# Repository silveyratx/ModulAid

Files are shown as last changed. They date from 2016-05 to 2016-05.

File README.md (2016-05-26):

# Modulaid

### Overview
ModulAid was born at UT Austin as a Senior Design Project for 5 Electrical Engineering [students](#contributors). Their senior design class was a special section called "Startup Senior Design" and the students thought up their own project rather than doing an industry or faculty sponsored project.

ModulAid extends a smartphone by providing an easy to use interface for many different types of sensors. The main hub plugs into the smartphone via the headphone jack. Through the connection with the headphone jack, the board is able to communicate with the iOS app as well as harvest power. Sensors can then be attached to the shared sensor board. The board acquires data from the sensors, transmits it to the smartphone, and from there it is displayed to the user.

The team chose to focus on making ModulAid a system for medical devices. The ModulAid app was designed to make access to health information very cheap. The team wanted to make it as easy as possible for people to get insights about their own health and the health in their communities.

### Hardware
Our initial development was done on the NXP Quick-Jack development kit. Then we designed a 2.4 x 1.45 inch PCB, shown below. The Quick-Jack acted as our reference design but with unnecessary components removed and additional components added to satisfy design requirements.

Connecting the board with the phone is as simple as plugging it into the headphone jack. All communication with the phone is done through the four-terminal headphone jack. The four pins in the headphone jack are left audio, right audio, microphone, and ground.

The right audio channel is dedicated to transferring power through a constant audio wave. The signal is fed into a voltage rectifier that converts the low voltage AC signal into a higher voltage DC signal. The DC voltage is fed into a 3.3V regulator that produces a constant voltage for the microcontroller and sensors. The max power that can be harvested from the phone is about 15mW, but the exact value varies from phone to phone. The board also has a CR2032 battery on the back. When additional current is needed for a sensor, it can be drawn from the battery.

Besides providing power to the sensors, the board must be able to communicate with them. We created our own sensor interface so that all our sensors connect through the same port. All our compatible sensors fall into two categories, either those that produce an analog voltage signal or those that communicate through a peripheral on the microcontroller. We added a 2 channel 10-bit ADC (MCP3002) and a dual SPDT (single pole double throw) analog switch (TS3A24157). The signal lines from the sensor port connect to the common inputs of the SPDT switch. The firmware controls the input to the switch to either connect the sensor signals to the ADC or directly to the microcontroller. The schematic is included in the Hardware directory.

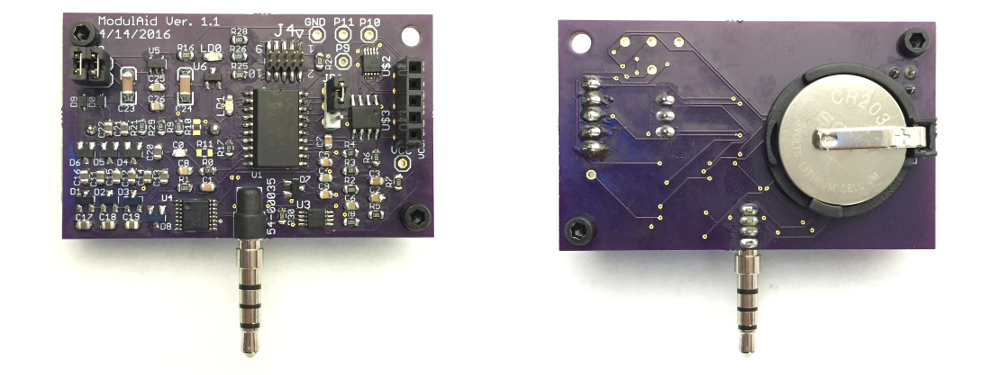
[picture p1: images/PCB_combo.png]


### Firmware
The firmware runs on the microcontroller(NXP LPC812) of the ModulAid board. The purpose of the firmware is to create a channel of communication between the smartphone and the various sensors. The firmware receives commands from the smartphone, initializes the hardware, acquires data, and sends the data to the smartphone. Upon reset of the device, the firmware performs the needed initialization for the device, then waits to receive a command from the phone. The command tells the firmware which sensor the user has selected. This is necessary because each sensor communicates with the board differently and requires a unique initialization. For example, the board uses I2C (Inter-Integrated Circuit) to communicate with the IR thermometer, but reads a voltage through the ADC (Analog to Digital Converter) with SPI (Serial Peripheral Interface) for the pulse sensor.

To use the ADC, first we must set the input to the dual SPDT switch such that the sensor wires connect to the inputs of the ADC. We then can sample the ADC by sending a command through SPI to the ADC. The command wakes up the ADC from its sleep state. From there it samples the requested input channel and sends the 10 bit result back. For some sensors, the raw ADC value might be a meaningful piece of data, but in the case of the pulse sensor we must take periodic readings that can be processed into a heart rate in beats per minute (BPM). The pulse sensor readings create a pulse wave. We calculate the BPM by measuring the time between peaks of the waves. The firmware keeps a running average of the BPM and when requested send the value to the smartphone.

For all sensors that don’t make use of the ADC, the input to the dual SPDT switch is set such that the signals from the sensor connect directly to the pins of the microcontroller. The microcontroller, the NXP LPC812, has an internal switch matrix that allows the hardware peripherals to be connected to almost any chosen pin. Because of this switch matrix, we can use the same set of pins for various communication protocols. When the IR thermometer is connected, the firmware assigns the I2C function to the sensor pins. Through the I2C bus, we can poll the thermometer for its most recent temperature reading.

The current hardware revision supports sensors that output an analog voltage or communicate through I2C or UART. SPI could be used for sensor communication if one more signal line was added between the microcontroller and the sensor port.

### iOS Application
The application user interface is the main “face” of the product for a user. Our goal in designing the user interface was to make the application so easy to use that it required no instruction. To accomplish this goal, we decided to use pictures rather than words whenever possible. This way, people of different cultures could use the same version of the app. Screenshots of are included below.

The user interface has three views that carry out the main functions of the application. There is a Home view, a Heatmap view, and a History. The Home view is where the user goes to take a measurement. From the Home view initial screen, the user selects which type of measurement they want to take. After the user selects their device, they are guided by a series of visual prompts to take the reading. In Heatmap view, the user can see what other ModulAid activity is happening around them. The Heatmap shows the locations and relative temperatures of other users. The heatmap is one example of real time health analytics that ModulAid offers, and in the future, it could be used to analyze the health in communities. In History view, a user can see the recent sensor measurements that were taken locally on their personal device.

All collected data is stored anonymously to a FireBase database. Along with the data point we store the location. Further insights and analytics could be generated from this data. The heatmap is one example of this, providing a way to plot the location and severity of fever on a map.

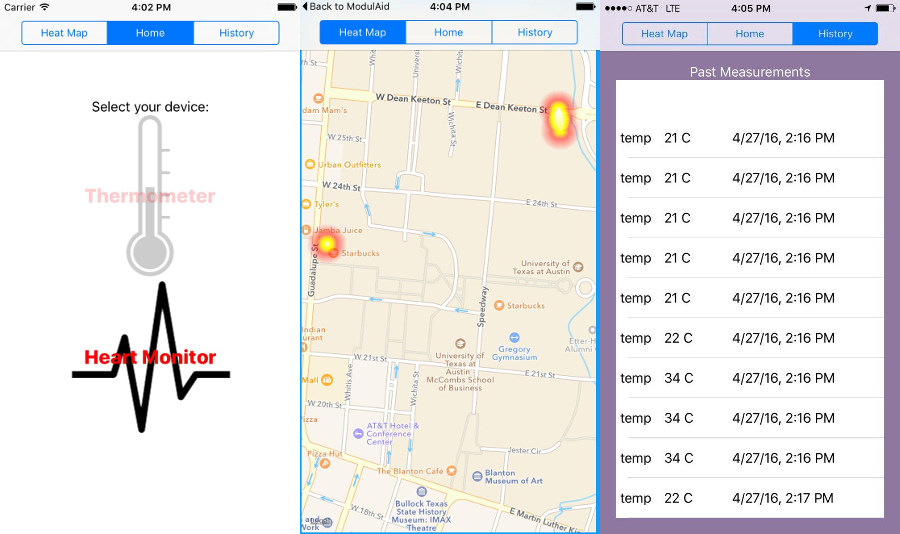
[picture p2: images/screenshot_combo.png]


### Demo
Here is a short video demonstrating the functionality: https://vimeo.com/168209562

### Going Forward
Due to the project’s scope in the Senior Design class, ModulAid only supports two sensors, a thermometer, and a heart rate monitor. There are many ways the project could move forward:      
	-Add support for additional sensors     
	-Create user accounts to give more specialized health insights      
	-Create an Android app similiar to the iOS app       
	-Rework the firmware to deal with sensors in a more generic way, allowing new sensors to be added without updating the firmware.    
-and probably many more..

We created this GitHub Repository to document our project and let it live on through the internet. We hope someone out there finds it useful, helpful or even inspiring. Furthermore, the platform is not limited to medical sensors and could be a base for interfacing all sorts of sensors with a smartphone.

### Resources
ModulAid draws from several projects and frameworks:

NXP QuickJack: http://www.nxp.com/products/microcontrollers-and-processors/arm-processors/lpc-cortex-m-mcus/lpc-cortex-m0-plus-m0-mcus/lpc800-low-cost-cortex-m0-plus-mcus/om13069-smartphone-quick-jack-solution:OM13069

LFHeatMap: https://github.com/gpolak/LFHeatMap

Firebase: https://www.firebase.com/

### Contributors
Alex Lee, Cage Johnson, Sam Moser, Alejandro Silveyra, and Ammar Hazim (in order of appearance)    
Photo of team at UT Austin Electrical and Computer Engineering Senior Design Open House - Spring 2016

We would also like to thank our faculty mentor, Ramesh Yerraballi, for his support through out the project.

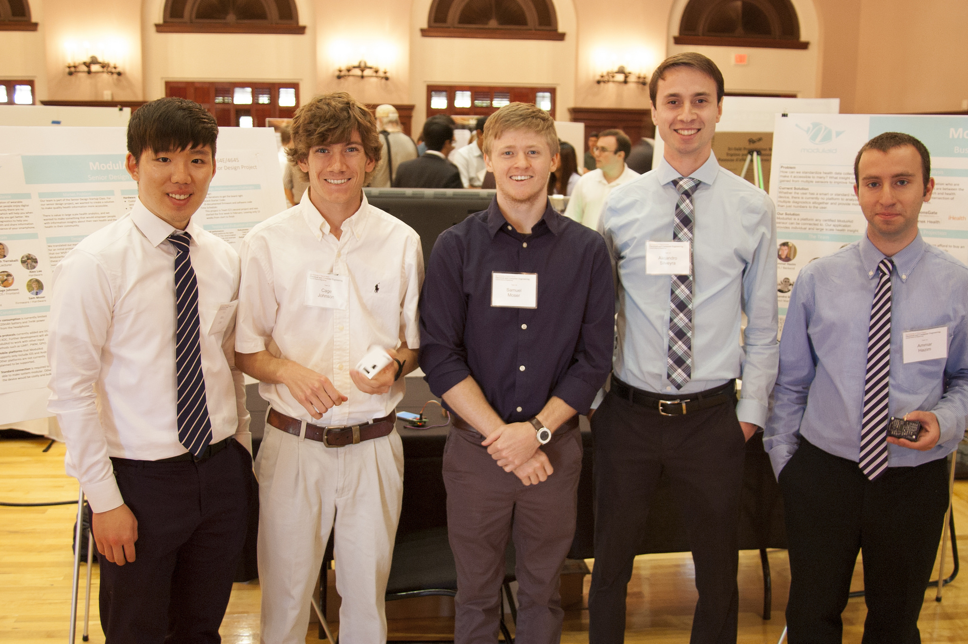
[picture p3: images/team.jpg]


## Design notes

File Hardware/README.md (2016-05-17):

# ModulAid Hardware

Schematic and PCB created in EagleCAD

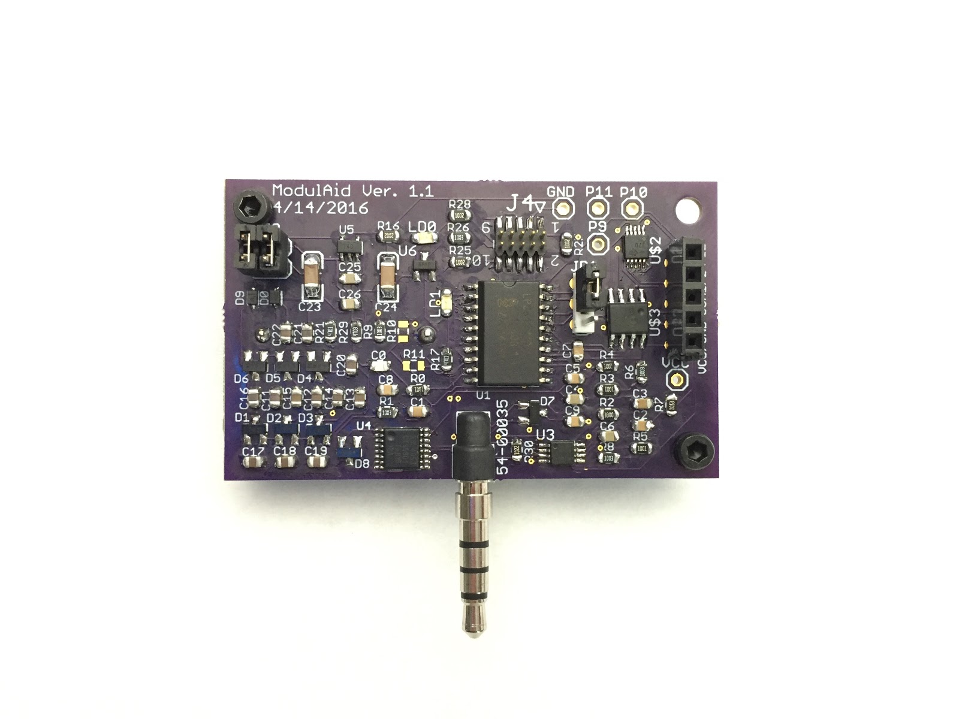
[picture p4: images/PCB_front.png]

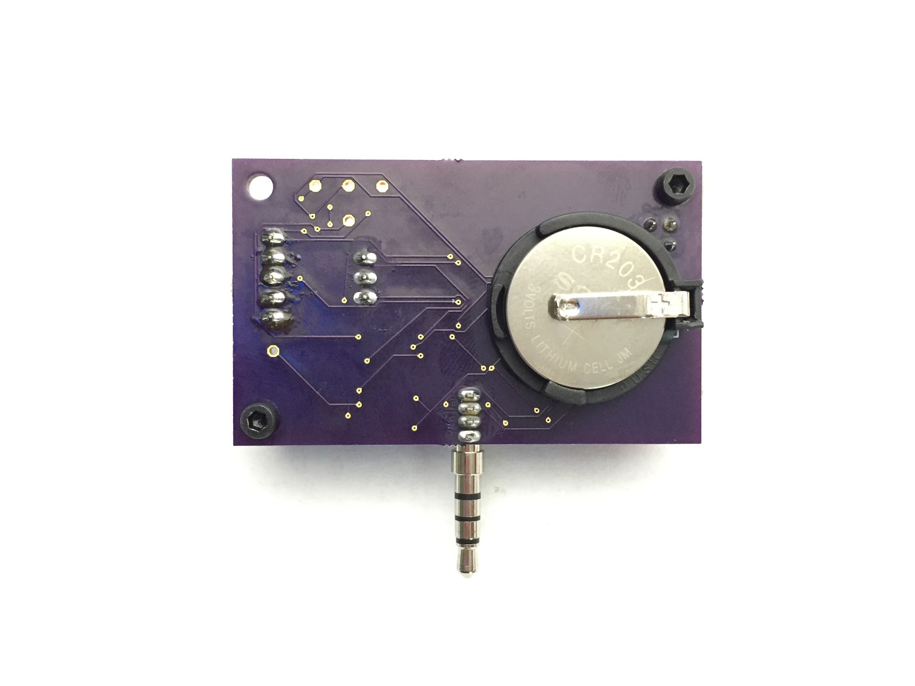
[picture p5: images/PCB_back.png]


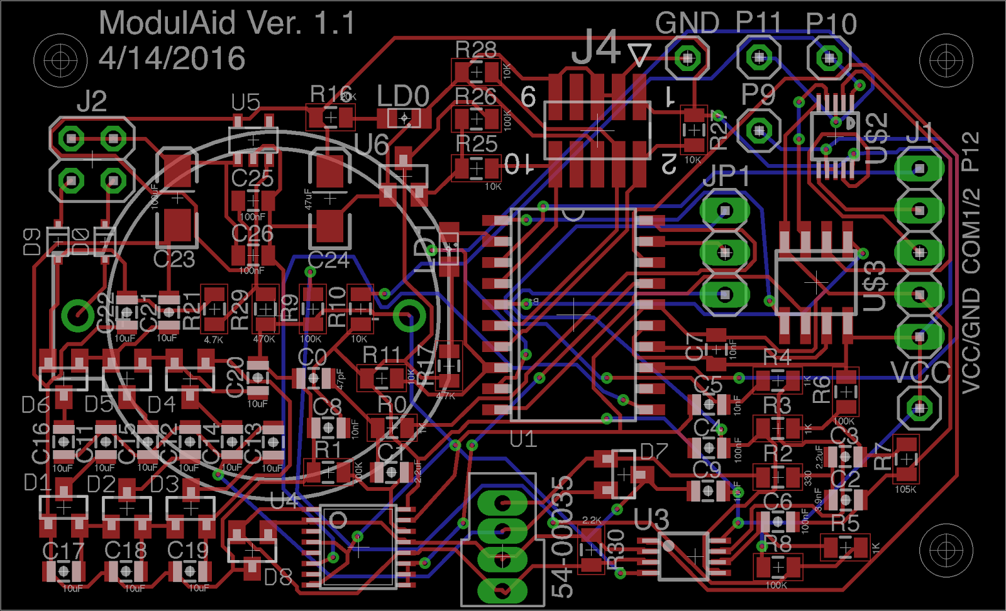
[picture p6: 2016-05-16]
images/PCB_schematic.png

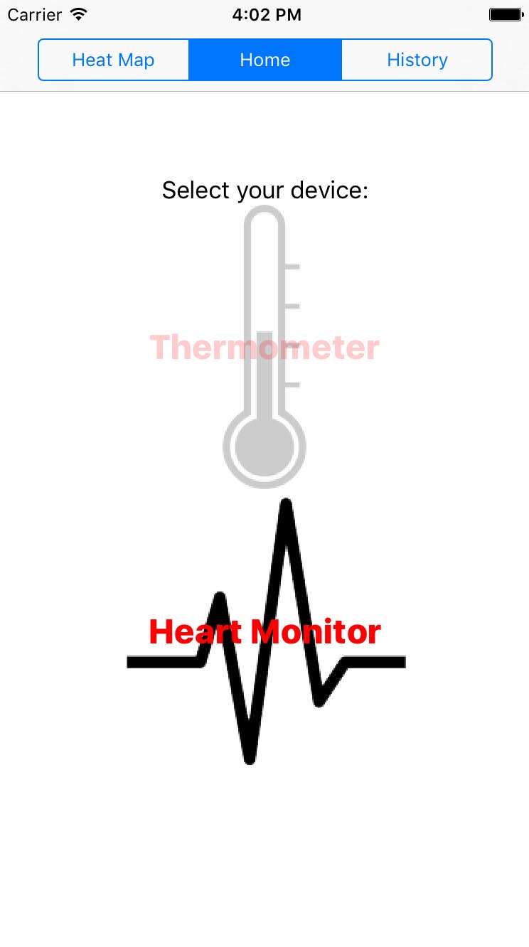
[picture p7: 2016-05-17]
images/iOS_mainscreen.png

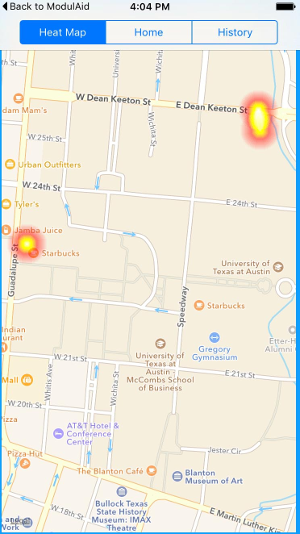
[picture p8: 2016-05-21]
images/iOS_heatmap_s.png

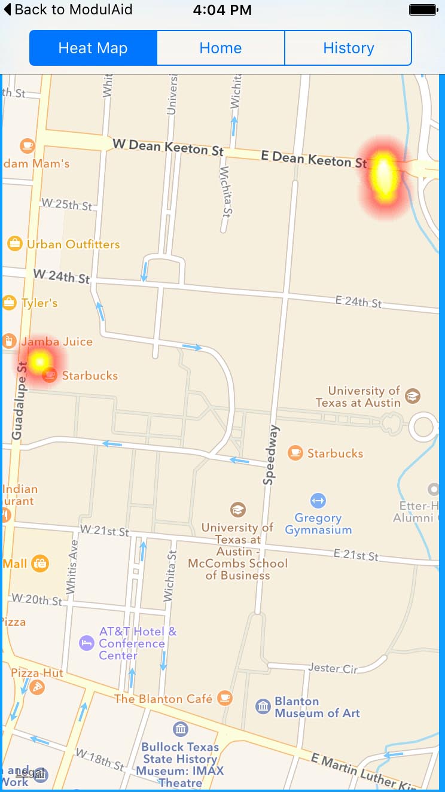
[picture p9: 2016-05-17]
images/iOS_heatmap.png

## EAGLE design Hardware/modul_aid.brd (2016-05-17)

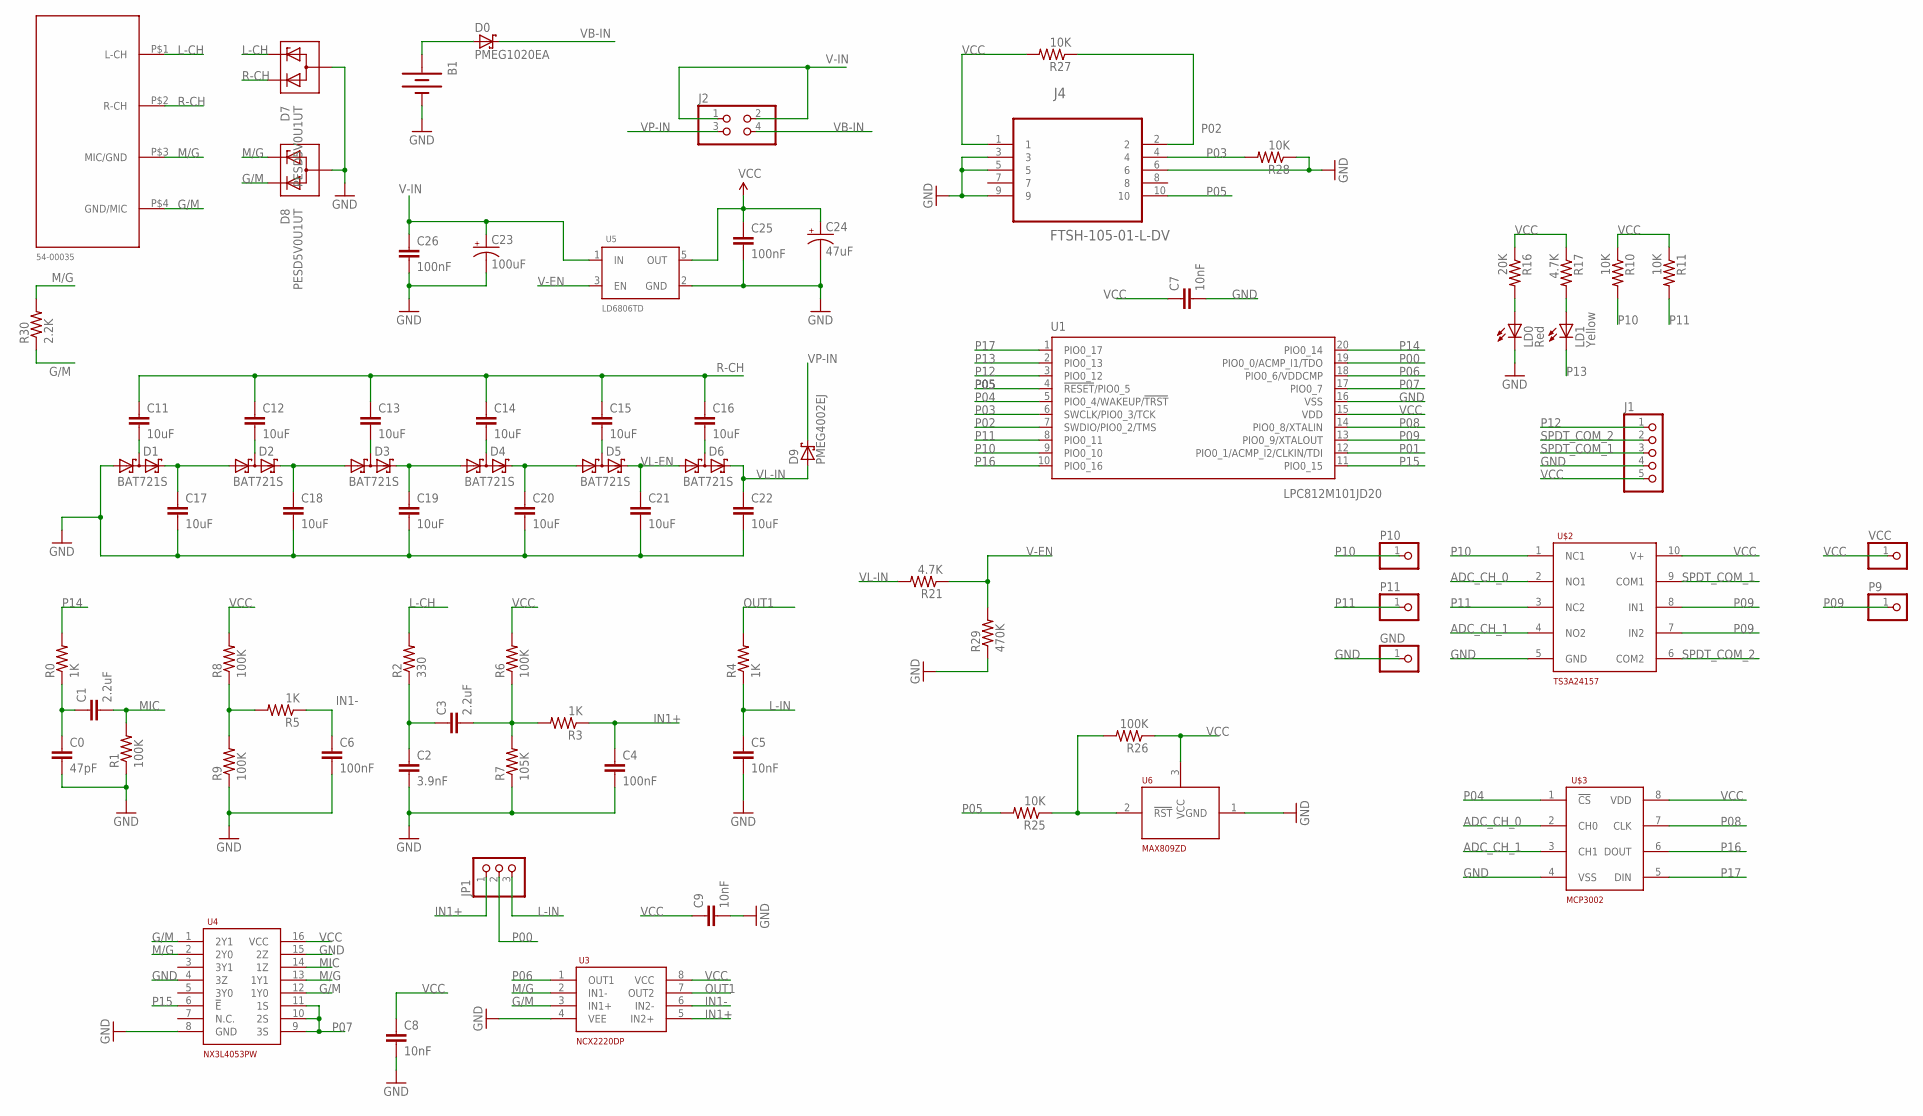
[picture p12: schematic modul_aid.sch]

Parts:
B1: BATTERY20PTH; BATTCOM_20MM_PTH
C0: 47pF; 0805-CAP
C1, C3: 2.2uF; 0805-CAP
C2: 3.9nF; 0805-CAP
C4, C6: 100nF; 0805-CAP
C5, C8, C9: 10nF; 0805-CAP
C7: 10nF; 0805
C11, C12, C13, C14, C15, C16, C17, C18, C19, C20, C21, C22: 10uF; 0805-CAP
C23: 100uF; EIA3216-KIT
C24: 47uF; EIA3216-KIT
C25, C26: 100nF; 0805
D0: PMEG1020EA; SOD323(F)
D1, D2, D3, D4, D5, D6: BAT721S; SOT23
D7, D8: PESD5V0U1UT; SOT23
D9: PMEG4002EJ; SOD323(F)
GND: PINHD-1X1; 1X01
J1: PINHD-1X5; 1X05
J2: PINHD-2X2; 2X02
J4: FTSH-105-01-L-DV; SAMTEC_FTSH-105-01-L-DV
JP1: PINHD-1X3; 1X03
LD0: Red; SML0805
LD1: Yellow; SML0805
P9, P10, P11: PINHD-1X1; 1X01
R0, R3, R4, R5: 1K; 0805
R1, R6, R8, R9, R26: 100K; 0805
R2: 330; 0805
R7: 105K; 0805
R10, R11, R25, R27, R28: 10K; 0805
R16: 20K; 0805
R17, R21: 4.7K; 0805
R29: 470K; 0805
R30: 2.2K; 0805
U1: LPC812M101JD20; SOT163-1
U3: NCX2220DP; SOT505-2
U4: NX3L4053PW; S0T403-1
U5: LD6806TD; SOT753
U6: MAX809ZD; SOT23-3
U$2: TS3A24157; VSSOP-10
U$3: MCP3002; SOIC8
U$4: TENSILITY54-00035; EE464SAUDIOJACK
VCC: PINHD-1X1; 1X01

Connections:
ADC_CH_0: U$2.2 (NO1), U$3.2 (CH0)
ADC_CH_1: U$2.4 (NO2), U$3.3 (CH1)
G/M: D8.2 (KD), R30.1, U3.3 (IN1+), U4.1 (2Y1), U4.12 (1Y0), U$4.P$4 (GND/MIC)
GND: B1.2 (-), C0.2, C2.2, C4.2, C5.2, C6.2, C7.2, C8.2, C9.2, C17.2, C18.2, C19.2, C20.2, C21.2, C22.2, C23.C (-), C24.C (-), C25.2, C26.2, D1.1 (A1), D7.3 (CA), D8.3 (CA), GND.1, J1.4, J4.3, J4.5, J4.6, J4.9, LD0.C, R1.1, R7.1, R9.1, R28.1, R29.1, U1.16 (VSS), U3.4 (VEE), U4.4 (3Z), U4.8 (GND), U4.15 (2Z), U5.2 (GND), U6.1 (GND), U$2.5 (GND), U$3.4 (VSS)
IN1+: C4.1, JP1.1, R3.1, U3.5 (IN2+)
IN1-: C6.1, R5.1, U3.6 (IN2-)
L-CH: D7.1 (KESD), R2.2, U$4.P$1 (L-CH)
L-IN: C5.1, JP1.3, R4.1
M/G: D8.1 (KESD), R30.2, U3.2 (IN1-), U4.2 (2Y0), U4.13 (1Y1), U$4.P$3 (MIC/GND)
MIC: C1.2, R1.2, U4.14 (1Z)
unnamed: C11.2, D1.3 (K1A2)
unnamed: C12.2, D2.3 (K1A2)
unnamed: C13.2, D3.3 (K1A2)
unnamed: C14.2, D4.3 (K1A2)
unnamed: C15.2, D5.3 (K1A2)
unnamed: C16.2, D6.3 (K1A2)
unnamed: B1.1 (+), D0.2 (A)
unnamed: C0.1, C1.1, R0.1
unnamed: C17.1, D1.2 (K2), D2.1 (A1)
unnamed: C18.1, D2.2 (K2), D3.1 (A1)
unnamed: C19.1, D3.2 (K2), D4.1 (A1)
unnamed: C20.1, D4.2 (K2), D5.1 (A1)
unnamed: R5.2, R8.1, R9.2
unnamed: C2.1, C3.1, R2.1
unnamed: R25.1, R26.2, U6.2 (!RST)
unnamed: C3.2, R3.2, R6.1, R7.2
unnamed: LD0.A, R16.2
unnamed: LD1.A, R17.2
OUT1: R4.2, U3.7 (OUT2)
P00: JP1.2, U1.19 (PIO0_0/ACMP_I1/TDO)
P01: U1.12 (PIO0_1/ACMP_I2/CLKIN/TDI)
P02: J4.2, R27.1, U1.7 (SWDIO/PIO0_2/TMS)
P03: J4.4, R28.2, U1.6 (SWCLK/PIO0_3/TCK)
P04: U1.5 (PIO0_4/WAKEUP/!TRST!), U$3.1 (!CS)
P05: J4.10, R25.2, U1.4 (!RESET!/PIO0_5)
P06: U1.18 (PIO0_6/VDDCMP), U3.1 (OUT1)
P07: U1.17 (PIO0_7), U4.9 (3S), U4.10 (2S), U4.11 (1S)
P08: U1.14 (PIO0_8/XTALIN), U$3.7 (CLK)
P09: P9.1, U1.13 (PIO0_9/XTALOUT), U$2.7 (IN2), U$2.8 (IN1)
P10: P10.1, R10.2, U1.9 (PIO0_10), U$2.1 (NC1)
P11: P11.1, R11.2, U1.8 (PIO0_11), U$2.3 (NC2)
P12: J1.1, U1.3 (PIO0_12)
P13: LD1.C, U1.2 (PIO0_13)
P14: R0.2, U1.20 (PIO0_14)
P15: U1.11 (PIO0_15), U4.6 (!E)
P16: U1.10 (PIO0_16), U$3.6 (DOUT)
P17: U1.1 (PIO0_17), U$3.5 (DIN)
R-CH: C11.1, C12.1, C13.1, C14.1, C15.1, C16.1, D7.2 (KD), U$4.P$2 (R-CH)
SPDT_COM_1: J1.3, U$2.9 (COM1)
SPDT_COM_2: J1.2, U$2.6 (COM2)
V-EN: R21.1, R29.2, U5.3 (EN)
V-IN: C23.A (+), C26.1, J2.1, J2.2, U5.1 (IN)
VB-IN: D0.1 (K), J2.4
VCC: C7.1, C8.1, C9.1, C24.A (+), C25.1, J1.5, J4.1, R6.2, R8.2, R10.1, R11.1, R16.1, R17.1, R26.1, R27.2, U1.15 (VDD), U3.8 (VCC), U4.16 (VCC), U5.5 (OUT), U6.3 (VCC), U$2.10 (V+), U$3.8 (VDD), VCC.1
VL-EN: C21.1, D5.2 (K2), D6.1 (A1)
VL-IN: C22.1, D6.2 (K2), D9.2 (A), R21.2
VP-IN: D9.1 (K), J2.3

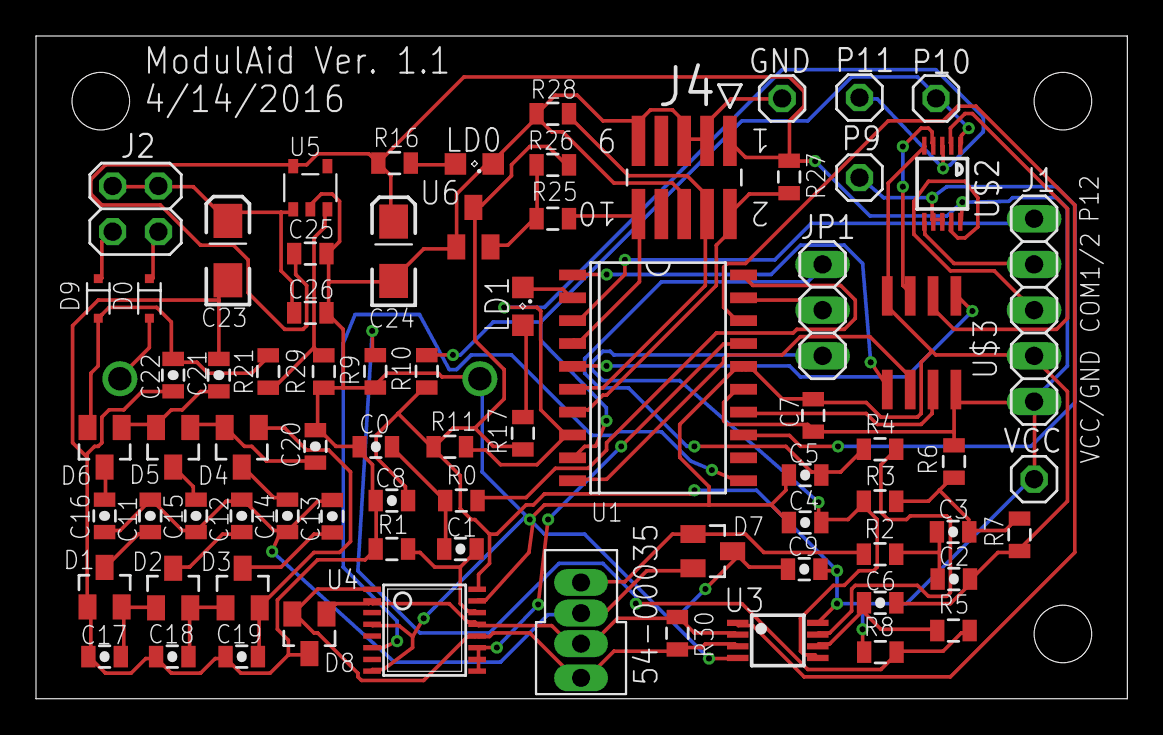
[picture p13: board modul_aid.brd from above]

Board: 2 copper layers, 60.6 x 36.8 mm, 77 parts (1 on the bottom side), 56 nets.

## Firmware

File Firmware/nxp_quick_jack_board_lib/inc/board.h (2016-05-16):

/*
 * @brief NXP_Quick_Jack board (LPC812) board file
 *
 * @note
 * Copyright(C) NXP Semiconductors, 2014
 * All rights reserved.
 *
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
 * @par
 * Permission to use, copy, modify, and distribute this software and its
 * documentation is hereby granted, under NXP Semiconductors' and its
 * licensor's relevant copyrights in the software, without fee, provided that it
 * is used in conjunction with NXP Semiconductors microcontrollers.  This
 * copyright, permission, and disclaimer notice must appear in all copies of
 * this code.
 */

#ifndef __BOARD_H_
#define __BOARD_H_

#include "chip.h"
/* board_api.h is included at the bottom of this file after DEBUG setup */

#ifdef __cplusplus
extern "C" {
#endif



/***** Sam's Additions ******************/
#define LEDHEARTBEAT 13

#define DUALSWTCHINPUT	9
#define DUALSWTCHNC1	10
#define DUALSWTCHNC2	11
#define THIRDSENSORPIN	12
#define THERMSCL DUALSWTCHNC1
#define THERMSDA DUALSWTCHNC2

// MLX90614 constants
#define MLX90614_DEFAULT_ADDRESS_W	0xB4
#define MLX90614_DEFAULT_ADDRESS_R	0xB5
#define MLX90614_REGISTER_TA		0x06
#define MLX90614_REGISTER_TOBJ1		0x07

void SensorSwitch_ConnectToUc(void);
void SensorSwitch_ConnectToADC(void);
void IrTherm_Init(void);
int32_t IrTherm_Read(void);
uint32_t SPI_ReadCh0(void);
bool Pulse_IsNewData(void);
uint16_t Pulse_GetBPM(void);
void PulseInterrupt(void);
/*****************************************/

/** @defgroup BOARD_LPC812QUICKJACK (LPC812) board support software API functions
 * @ingroup LPCOPEN_8XX_LPC812 NXP_Quick_Jack
 * The board support software API functions provide some simple abstracted
 * functions used across multiple LPCOpen board examples. See @ref BOARD_COMMON_API
 * for the functions defined by this board support layer.<br>
 * @{
 */

/** @defgroup BOARD_LPC812QUICKJACK OPTIONS BOARD: NXP_Quick_Jack board (LPC812) board build options
 * This board has options that configure its operation at build-time.<br>
 * @{
 */

/* 1Mbps I2C bit-rate */
//#define I2C_BITRATE											(400000)
#define I2C_BITRATE											(100000)

/* For more info, read NXP's Se98 datasheet */
#define SE98_ADDR												0x38
#define SE98_ID													0x06
#define SE98_TEMP												0x05

/**
 * @brief NXP Quick-Jack Application function - NXP Quick-Jack application hardware
 */
/*!< LED numbers declaration */
#define LED1Num														0
#define LED2Num														1
#define LED3Num														2
#define LED4Num														3

//Hi-jack APP func
//JoyStick Func
#define LED1_PINNUM											8
#define LED2_PINNUM											9
#define LED3_PINNUM											12
#define LED4_PINNUM											13

#define K_Up_PINNUM											11
#define K_Down_PINNUM										17
#define K_Left_PINNUM										16
#define K_Right_PINNUM									4
#define K_Press_PINNUM									10


/*!< PIO0_14 The Pin for MCU transfer data to Mobile */
#define QUICKJACKTXPIN										IOCON_PIO14
#define QUICKJACKTXPINNUM									14
/*!< PIO0_0  The Pin for MCU receive data from Mobile */
#define QUICKJACKRXPIN										IOCON_PIO0
/*!< PIO0_6  The pin for MIC and GND comparative result */
#define MnGACMPOUTPIN											IOCON_PIO6 
#define MnGACMPOUTPINNUM									6																										
/*!< PIO0_7  The pin for Analog switch selection */
/*!< (output low 3: MIC, 4: GND; output low 3: GND, 4: MIC) */
#define MnGSWSELPIN												IOCON_PIO7	
#define MnGSWSELPINNUM										7	
/*!< PIO0_15 The pin for Analog switch enabled */
/*!< (output low enabled the SW)*/
#define MnGSWENAPIN												IOCON_PIO15 
#define MnGSWENAPINNUM										15	
/*!< PININT channel number of Manchester RX pin */
#define PININT_RXPIN_CHAN_NUM							0

/**
 * @}
 */

/* Board name */
#define BOARD_LPC812QUICKJACK

/**
 * @}
 */

#include "board_api.h"

#ifdef __cplusplus
}
#endif

#endif /* __BOARD_H_ */

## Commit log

2016-05-17 added schematic and pcb files
    [modul_aid.brd, modul_aid.sch]
2016-05-21 added heatmap screenshot
2016-05-21 smaller heatmap screenshot
2016-05-21 fixed paths to pcb images
2016-05-21 pcb combo photo added
2016-05-21 moved pcb photo

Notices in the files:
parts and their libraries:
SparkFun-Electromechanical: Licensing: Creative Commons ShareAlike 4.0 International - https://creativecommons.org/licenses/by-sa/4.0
